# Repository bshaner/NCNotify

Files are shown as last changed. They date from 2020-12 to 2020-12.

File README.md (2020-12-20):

# NCNotify-Core

*This project is a work-in-progress with a focus on learning, if you have suggestions or expertise to share, drop me a line!*

A nurse call BNC data logger, designed to work with any normally-open BNC nurse call system. I used publicly available datasheets and promo materials for the Airon pNeuton transport ventilator as a guide, but don't have one to test with. A test jig is coming (check the Documentation folder ... soon).

## Development
Permanent branches will be used for alternate layout ideas, pared-down implementations, or implementations with extra peripherals. Parens are used for branches I plan to start, but haven't jumped into:

* main: core development branch, on track for fab and assemble runs. Includes development headers, jumpers, no peripherals
* (bluetooth: bluetooth peripheral incl. Easy to integrate, but requires tighter power management (2 mcu). I'm interested in trying an all-nordic board down the road as a complete redesign, maybe with a wall-wart base station BT->Wi-Fi/Ethernet bridge)
	
## Principle of operation:
- Board runs on coin cell as fully pneumatic, mobile ventilator cannot supply power
- Nurse call connection (BNC-F) is normally-closed with an fairly high internal resistance (e.g. 51KOhm)
- MCU wakes regularly to poll the state of the nurse call relay, logging the state in flash with relative timestamps
- MCU offloads logging data to PC via USB to custom application, which translates events to absolute timestamps
	
## Other features/design goals:
- Battery status LED lights when Batt button is pressed, steady light for good battery health, flashing for low battery health
- Power optimization is a goal for firmware and design, aiming for months of operation on coin cell. Big concerns are 
	- cap leakage (decoupling caps likely to be removed/not populated), 
	- peak current consumption when polling/writing flash, 
	- deep sleep states vs timers needed for wakeup and timestamping events
	- current management for status LED over [~2.3?, 3.3]V given relatively large forward voltage drop
- Power from USB when available
	- Approach here was to try using a switch to detect when USB is plugged, because protection diodes and pmosfet would cause voltage drop and reduce battery life. But it is too big. Fun to try anyway!
	- Until a new solution comes up, jumpers will be used for USB vs BATT power mode, so testing doesn't use too many batteries
- Single-sided SMD assembly

## Known issues
	v1.0
		- SWD CLK and DIO are swapped

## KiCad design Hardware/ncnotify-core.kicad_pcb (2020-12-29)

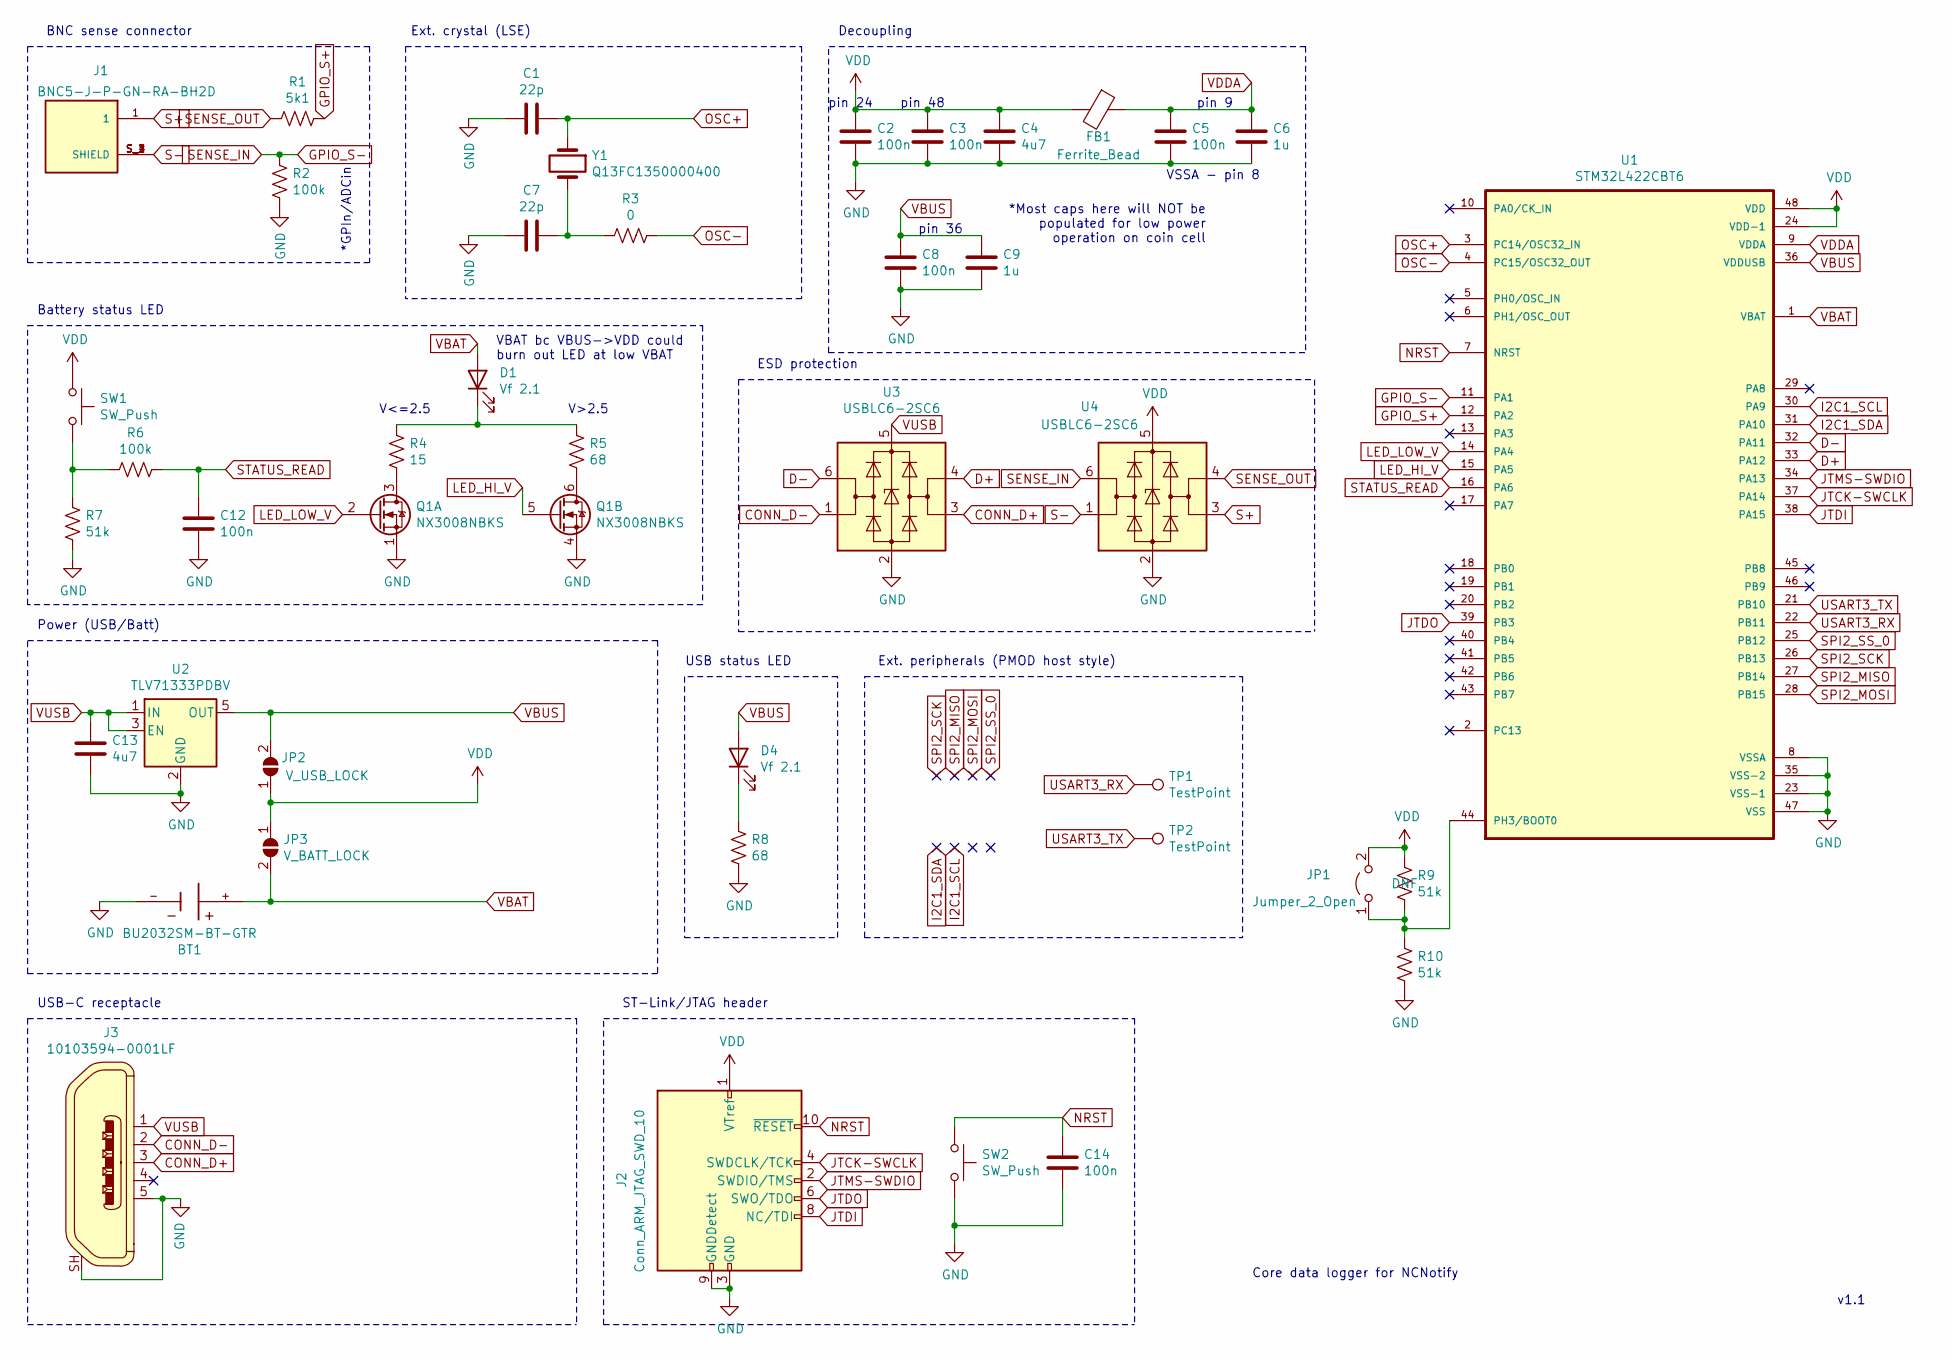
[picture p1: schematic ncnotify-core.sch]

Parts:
BT1: BU2032SM-BT-GTR; BAT_BU2032SM-BT-GTR; PARTREV F
C1, C7: 22p; C_0402_1005Metric; LCSC Part # C1555
C2, C3, C5, C8, C12, C14: 100n; C_0402_1005Metric; LCSC Part # C1525
C4, C13: 4u7; C_0603_1608Metric; LCSC Part # C19666
C6, C9: 1u; C_0402_1005Metric; LCSC Part # C52923
D1, D4: Vf ~ 2.1; LED_0603_1608Metric; LCSC Part # C72038
FB1: Ferrite_Bead; L_0805_2012Metric; LCSC Part # C1015
J1: BNC5-J-P-GN-RA-BH2D; SAMTEC_BNC5-J-P-GN-RA-BH2D; PARTREV C
J2: Conn_ARM_JTAG_SWD_10; PinHeader_2x05_P1.27mm_Vertical
J3: 10103594-0001LF; USB_Micro_B_Female_10103594-0001LF; MPN 10103594-0001LF; Digi-Key_PN 609-4050-1-ND
JP1: Jumper_2_Open; PinHeader_1x02_P1.27mm_Vertical
JP2: V_USB_LOCK; SolderJumper-2_P1.3mm_Open_TrianglePad1.0x1.5mm
JP3: V_BATT_LOCK; SolderJumper-2_P1.3mm_Open_TrianglePad1.0x1.5mm
Q1: NX3008NBKS; SOT-363; LCSC Part # C396098
R1: 5k1; R_0402_1005Metric; LCSC Part # C25905
R2, R6: 100k; R_0402_1005Metric; LCSC Part # C25741
R3: 0; R_0402_1005Metric; LCSC Part # C17168
R4: 15; R_0603_1608Metric; LCSC Part # C22810
R5, R8: 68; R_0603_1608Metric; LCSC Part # C27592
R7, R9, R10: 51k; R_0402_1005Metric; LCSC Part # C25794
SW1, SW2: SW_Push; TS-1187A; LCSC Part # C318884
TP1, TP2: TestPoint; TestPoint_Pad_D1.5mm
U1: STM32L422CBT6; QFP50P900X900X160-48N; LCSC Part # C94785
U2: TLV71333PDBV; SOT-23-5; LCSC Part # C90840
U3, U4: USBLC6-2SC6; SOT-23-6; LCSC Part # C7519
Y1: Q13FC1350000400; Crystal_SMD_3215-2Pin_3.2x1.5mm; LCSC Part # C32346

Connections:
CONN_D+: J3.3, U3.3 (I/O2)
CONN_D-: J3.2, U3.1 (I/O1)
D+: U1.33 (PA12), U3.4 (I/O2)
D-: U1.32 (PA11), U3.6 (I/O1)
GND: BT1.-, C1.2, C2.2, C3.2, C4.2, C5.2, C6.2, C7.2, C8.2, C9.2, C12.2, C13.2, C14.2, J2.3 (GND), J2.5 (GND), J2.9 (GNDDetect), J3.5, J3.SH, Q1.1 (S), Q1.4 (S), R2.1, R7.2, R8.2, R10.2, SW2.2, U1.8 (VSSA), U1.23 (VSS-1), U1.35 (VSS-2), U1.47 (VSS), U2.2 (GND), U3.2 (GND), U4.2 (GND)
GPIO_S+: R1.1, U1.12 (PA2)
GPIO_S-: R2.2, U1.11 (PA1), U4.6 (I/O1)
I2C1_SCL: U1.30 (PA9)
I2C1_SDA: U1.31 (PA10)
JTCK-SWCLK: J2.4 (SWDCLK/TCK), U1.37 (PA14)
JTDI: J2.8 (NC/TDI), U1.38 (PA15)
JTDO: J2.6 (SWO/TDO), U1.39 (PB3)
JTMS-SWDIO: J2.2 (SWDIO/TMS), U1.34 (PA13)
LED_HI_V: Q1.5 (G), U1.15 (PA5)
LED_LOW_V: Q1.2 (G), U1.14 (PA4)
NRST: C14.1, J2.10 (~RESET~), SW2.1, U1.7 (NRST)
unnamed: C7.1, R3.1, Y1.2
unnamed: D1.1 (K), R4.1, R5.1
unnamed: D4.1 (K), R8.1
unnamed: JP1.1 (A), R9.2, R10.1, U1.44 (PH3/BOOT0)
unnamed: Q1.3 (D), R4.2
unnamed: Q1.6 (D), R5.2
unnamed: R6.2, R7.1, SW1.2
OSC+: C1.1, U1.3 (PC14/OSC32_IN), Y1.1
OSC-: R3.2, U1.4 (PC15/OSC32_OUT)
S+: J1.1, U4.3 (I/O2)
S-: J1.S_1 (SHIELD), J1.S_2 (SHIELD), J1.S_3 (SHIELD), J1.S_4 (SHIELD), U4.1 (I/O1)
SENSE_OUT: R1.2, U4.4 (I/O2)
SPI2_MISO: U1.27 (PB14)
SPI2_MOSI: U1.28 (PB15)
SPI2_SCK: U1.26 (PB13)
SPI2_SS_0: U1.25 (PB12)
STATUS_READ: C12.1, R6.1, U1.16 (PA6)
USART3_RX: TP1.1, U1.22 (PB11); also elsewhere on the board
USART3_TX: TP2.1, U1.21 (PB10)
VBAT: BT1.+, D1.2 (A), JP3.2 (B), U1.1 (VBAT)
VBUS: C8.1, C9.1, D4.2 (A), JP2.2 (B), U1.36 (VDDUSB), U2.5 (OUT)
VDD: C2.1, C3.1, C4.1, FB1.2, J2.1 (VTref), JP1.2 (B), JP2.1 (A), JP3.1 (A), R9.1, SW1.1, U1.24 (VDD-1), U1.48 (VDD), U4.5 (VBUS)
VDDA: C5.1, C6.1, FB1.1, U1.9 (VDDA)
VUSB: C13.1, J3.1, U2.1 (IN), U2.3 (EN), U3.5 (VBUS)

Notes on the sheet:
Ext. crystal (LSE)
BNC sense connector
USB-C receptacle
Power (USB/Batt)
ST-Link/JTAG header
Battery status LED
Decoupling
*GPIn/ADCin
USB status LED
V<=2.5
V>2.5
VBAT bc VBUS->VDD could burn out LED at low VBAT
ESD protection
Ext. peripherals (PMOD host style)
VSSA - pin 8
pin 9
pin 36
pin 48
pin 24
*Most caps here will NOT be populated for low power operation on coin cell
Core data logger for NCNotify
v1.1

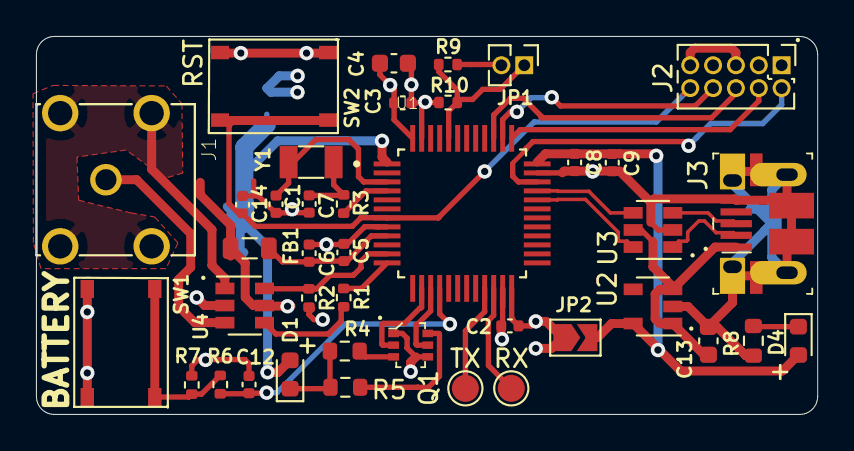
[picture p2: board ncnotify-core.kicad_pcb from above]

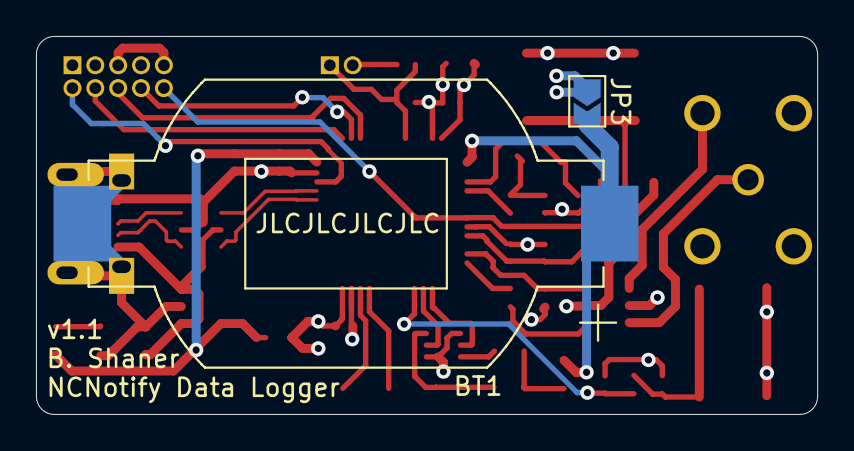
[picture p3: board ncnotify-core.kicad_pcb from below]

Board: 4 copper layers, 43.4 x 21.0 mm, 42 parts (2 on the bottom side), 34 nets.

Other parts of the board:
TPE: TestPoint; TestPoint_Pad_D1.5mm

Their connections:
USART3_RX: TPE.1; also elsewhere on the board

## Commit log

2020-11-29 Schematic and rough placement
    [ncnotify-core.kicad_pcb, ncnotify-core.sch]
2020-11-29 Remove switches and expansion header
    [ncnotify-core.kicad_pcb, ncnotify-core.sch]
2020-11-30 Routing and replaced USB ESD chip
    [ncnotify-core.kicad_pcb, ncnotify-core.sch]
2020-11-30 lcsc part numbers for bom, cleanup before trying gerbers
    [ncnotify-core.kicad_pcb, ncnotify-core.sch]
2020-12-01 Cleanup silkscreen, add part numbers to sch bom
    [ncnotify-core.kicad_pcb, ncnotify-core.sch]
2020-12-01 bump to developing version v1.1
    [ncnotify-core.kicad_pcb, ncnotify-core.sch]
2020-12-02 Fix SWD CLK/DIO pin swap, add UART test points
    [ncnotify-core.kicad_pcb, ncnotify-core.sch]
2020-12-11 Board shrink; swap to RA BNC mount
    [ncnotify-core.kicad_pcb, ncnotify-core.sch]
2020-12-16 sizeup batt to 2032 for current limit; re-place to fit
    [ncnotify-core.kicad_pcb, ncnotify-core.sch]
2020-12-20 Resolve TH conflicts; add 3d models
    [ncnotify-core.kicad_pcb, ncnotify-core.sch]
2020-12-29 micro-usb connector
    [ncnotify-core.kicad_pcb, ncnotify-core.sch]
